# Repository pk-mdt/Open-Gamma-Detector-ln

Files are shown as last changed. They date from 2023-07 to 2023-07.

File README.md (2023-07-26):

# Open Gamma Detector

**This is a revised hardware design from the original 3.0 version of the project. The project has been redesigned in Kicad and incorporates an impedance controlled 4 layer board design, as well as micro SMA connectors to the SiPM**

These changed from the original project are hardware only, the original software works and has been fully tested on these revisions. Here is an assembled prototype with a Sodium Iodide Crystal from OST Photonics.

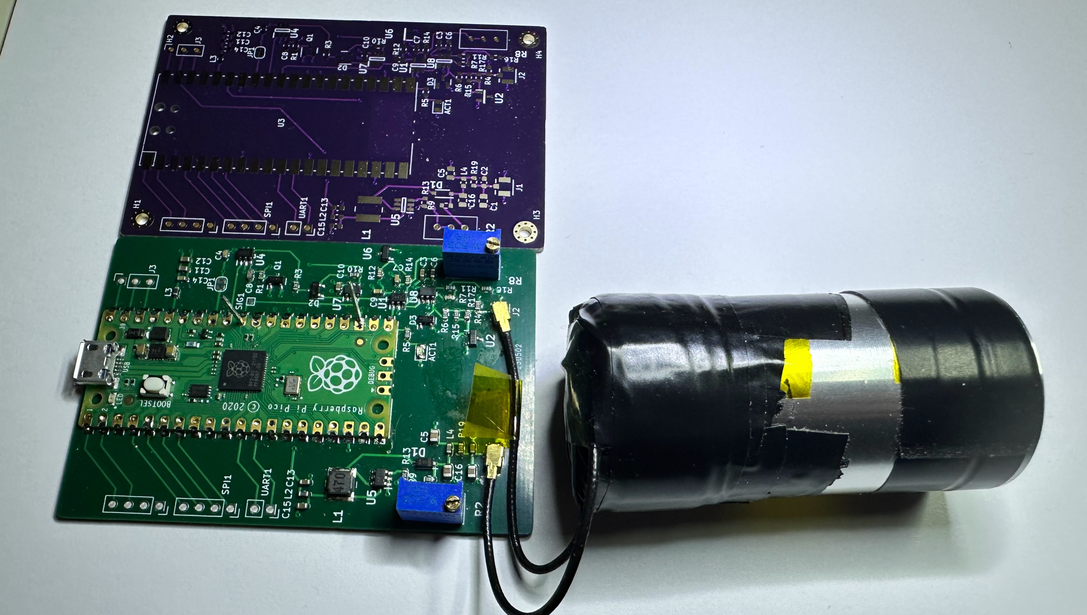
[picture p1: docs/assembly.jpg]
Assembled Detector and Latest Bare Board


Revised custom layout and hardware for a hackable scintillation counter and multichannel analyzer (MCA) all-in-one device using a popular NaI(Tl) scintillation crystal and a silicon photomultiplier (SiPM). Extremely affordable design for a DIY gamma spectroscopy setup with a total parts cost of under around 200 USD.

The detector uses a standard serial-over-USB connection so that it can be integrated into as many other projects as possible, for example data logging with a Raspberry Pi, weather stations, Arduino projects, etc.

If you want a barebone version of the Open Gamma Detector to count pulses or something like that, you can have a look at the [Mini SiPM Driver](https://github.com/OpenGammaProject/Mini-SiD) board.

## Features

Here are some of the most important specs:

* Compact design: Total size 77 x 50 mm.
* All-in-one: No external parts (e.g. sound card) required to record gamma spectra.
* Easily programmable using drag-and-drop firmware files or the standard Arduino IDE.
* Low-voltage device: No HV needed like with photomultiplier tubes.
* Can use SiPMs in the voltage range of 27.5 V to 33.8 V.
* 4096 ADC channels with built-in 3 V voltage reference.
* Revised Energy resolution of ~6% @ 662 keV possible; highly dependent on your SiPM/scintillator assembly.
* Default (Energy) Mode: About 15 µs total dead time while measuring energy.
* Geiger Mode: About 5 µs total dead time without energy measurements.
* Low power consumption: ~25 mA @ 5 V with default firmware.
* Additional broken-out power pins and I2C, SPI and UART headers for custom parts (e.g. display, µSD card, etc.).
* Built-in True Random Number Generator.
* Simple OLED support out of the box (SSD1306 and SH110x).
* Built-in customizable ticker support.

## Working Principle

Here is a nice flow chart to describe how the device roughly works:

Working Principle Flow Chart

## Hardware

Hardware design has been done with Kicad and all the needed files for you to import the project as well as the schematic can be found in the `hardware` folder. There is also a Gerber file available for you to go directly to the PCB manufacturing step.

Detailed information about the hardware of the detector as well as the potentiometer settings and assembly can be found in the [hardware directory](/hardware/).

## Software

The software aims to be as simple as possible to understand and maintain. To achieve this I decided to use an off-the-shelf microcontroller - the [Raspberry Pi Pico](https://www.raspberrypi.com/products/raspberry-pi-pico/). This board can be programmed with the Arduino IDE over micro-USB and is powerful (dual core, fast ADC, plenty of memory, ...) enough for the purpose and also exceptionally cheap.

To program the Pico and/or play around with the firmware, head to the [software directory](/software/). There you will also find documentation on the serial interface (!), display support, and much more.

## Example Spectra

Coming Soon

## Known Limitations

1. The Raspberry Pi Pico's ADC has some pretty [severe DNL issues](https://pico-adc.markomo.me/INL-DNL/#dnl) that result in four channels being much more sensitive (wider input range) than the rest. For now the simplest solution was to discard all four of them, by printing a `0` when any of them comes up in the measurement (to not affect the cps readings). You can turn this behavior off by using the `set correction` command. This is by no means perfect or ideal, but it works for now until this gets fixed in a later hardware revision of the RP2040 (wish us luck!).

2. Due to the global parts shortage many chips are much harder to come by, if at all that is. Parts that are listed in the BOM should be available easily and with high reliability and stock so that they don't run out quickly. Please let me know if you cannot find a part anymore.

3. The power supply is currently **not** temperature corrected, meaning changes in the ambient temperature with a constant voltage affect the gain of the SiPM. This will naturally result in a different DC bias, energy range and S/N ratio. This effect is negligible around room temperature, though. The temperature dependence of the gain is -0.8%/°C (21°C) for the MicroFC SiPMs.

## Troubleshooting and FAQ

Please have a look at [REFERENCE.md](REFERENCE.md) for some general guidance.

If this doesn't help you, feel free to reach out and create an issue or open a discussions thread.

## Some Ideas

### Coincidence Measurements

Using multiple detector boards with some firmware modifications it should be theoretically possible to implement a coincidence measurement feature. By respectively connecting the `VSYS`, `GND` and one of the broken-out pins to each other on both boards you have everything you need to get started. The pins would be used for an interrupt from the child detector to the parent to trigger a pulse if both timings coincide.

At the moment, though, I couldn't get a coincidence mode feature running due to some weird timing issues. There might be a firmware update in the future to implement this feature. If you have any ideas, let me know!

### Cooling the SiPM

During operation all the electronics including the SiPM naturally heat up ever so slightly. Due to the detector board (where most of the power is dissipated) not being directly connected to the SiPM self-heating is negligible, though. Therefore air or water cooling alone won't improve performance considerably, because it won't heat up much above ambient temps, if at all that is. However, you could cool the SiPM PCB with a Peltier module to sub-ambient temperatures. According to the [datasheet AND9770 (Figure 27)](https://www.onsemi.com/pub/Collateral/AND9770-D.PDF) every 10°C reduction in temperature decreases the dark count rate by 50%! But be sure to correct the SiPM voltage (overvoltage) in this case as it also changes with temperature.

Note that the required breakdown voltage of the SiPM increases linearly with 21.5 mV/°C, see the [C-Series SiPM Sensors Datasheet](https://www.onsemi.com/pdf/datasheet/microc-series-d.pdf). This means that you would also need to temperature correct the PSU voltage if you wanted to use it with considerably different temperatures.

### Shielding Background Radiation

Shielding the ambient background can be done ideally using a wide enough layer of lead (bricks) all around the detector with a thin layer of lower-Z material on the inside such as copper to avoid backscattering. The SiPM and the sample can then be put into the structure to get the best measurements possible (low background).

See Wikipedia: [Lead Castle](https://en.wikipedia.org/w/index.php?title=Lead_castle&oldid=991799816)

---

Thanks for reading.

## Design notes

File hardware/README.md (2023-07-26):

# Hardware

_Here you can find everything you need to build yourself a detector, or more._

This project utilizes a silicon photomultiplier (short SiPM) which is way smaller and more robust than a traditional photomultiplier tube and does not need a high-voltage supply (traditionally ~1000 V).

The following 6 mm SiPMs are recommended for this project:

* **MICROFC-60035-SMT-TR**
* MICROFC-60035-SMT-TR1 (the exact same as above, however will be more expensive to purchase as sold in smaller batches to suppliers)
* AFBR-S4N66C013 (a good replacement if the above are unavailable)

Here are some very helpful in-depth datasheets about the particular MicroFC SiPM recommended here:

* [C-Series SiPM Sensors datasheet](https://www.onsemi.com/pdf/datasheet/microc-series-d.pdf)
* [Linearity of the Silicon Photomultiplier](https://www.onsemi.com/pub/Collateral/AND9776-D.PDF)
* [Introduction to the SiliconPhotomultiplier (SiPM)](https://www.onsemi.com/pub/Collateral/AND9770-D.PDF)
* [Biasing and Readout of ON Semiconductor SiPM Sensors](https://www.onsemi.com/pub/Collateral/AND9782-D.PDF)

The hardware consists of the main detector (hardware in this folder) which includes amplification, pulse detection and energy measurement. If you already have a SiPM/crystal assembly compatible with voltages around 30 V, you may use it with the detector board and connecting wires directly to the correct pads. Otherwise, you can use my [SiPM carrier board](https://github.com/OpenGammaProject/MicroFC-SiPM-Carrier-Board), which holds the SiPM and all the optional decoupling. There is also a carrier board for the Broadcom SiPM.

The heart of the detector board is the Raspberry Pi Pico which uses its ADC to measure the pulse amplitude (i.e. the energy) immediately after an event occurs starting with an interrupt. I can really recommend you reading the datasheet or maybe also having a look at a deeper analysis of the Pico ADC, if you're interested:

* [Raspberry Pi Pico](https://datasheets.raspberrypi.com/pico/pico-datasheet.pdf)
* [Characterizing the Raspberry Pi Pico ADC](https://pico-adc.markomo.me/)

Here is sa front render of the detector PCB. Size is about 77 x 50 mm. 

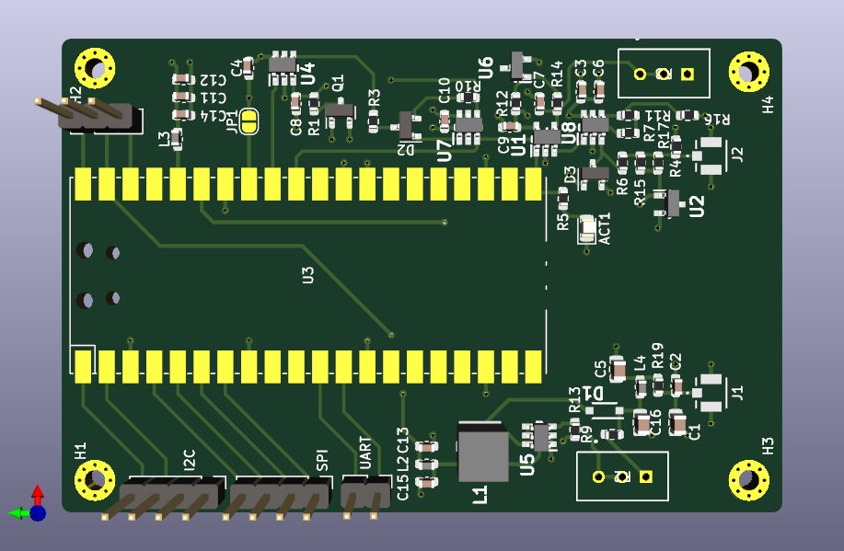
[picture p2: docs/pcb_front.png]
Front Side PCB


On the front side of the PCB at JP1 there is also a jumper to connect the analog ground to the rest of the ground plane. You can solder that if you want to, if you know exactly what you're doing. It's not needed, though.

There are also broken-out pins for the power supply, I2C, SPI and UART connections. These can be used to modify the device, e.g. by adding a display or using a battery charger. You can have a look at the great [Raspberry Pi Pico datasheet](https://datasheets.raspberrypi.com/pico/pico-datasheet.pdf) for more info on this.

Some more info on the peripheral headers can be found in the `software` section of this project.

## Pinout

Header Pinout

You can also put a little jumper from `VBUS` to `VSYS` if you **only** want to use the detector with the USB connection on the Pico. This bridges a diode on the Raspberry Pi Pico and saves you a couple of mW.

## Potentiometers

Here is a helpful image about the potentiometer settings for revision 3.0, it's not complicated:

Potentiometer Controls

As you can see it is pretty easy to set the required voltage and threshold. **As a general rule, turn any potentiometer clockwise to increase the parameters, turn anti-clockwise to decrease.**

## Scintillator (Assembly)

The finished [MicroFC-](https://github.com/OpenGammaProject/MicroFC-SiPM-Carrier-Board) and [AFBR-](https://github.com/OpenGammaProject/AFBR-SiPM-Carrier-Board) SiPM carrier boards are there to allow for easier packaging with the scintillator as well as to be reusable for different detectors as that's by far the single most expensive part and you'll want to use it as long as possible.

If you are using a larger-diameter scintillator, it might be better for you to use something like the [MicroFC SiPM Array Board](https://github.com/OpenGammaProject/MicroFC-SiPM-Array-Board), which has a 2x2 matrix of SiPMs resulting in 4x the active area. This can increase the energy resolution for large crystals.

### Scintillator Cyrstals

I got all of my scintillators (used NaI(Tl), LYSO, ...) on eBay. Just search for some keywords or specific types, you'll probably find something. Just be sure to look out for signs of wear and tear like scratches on the window or yellowing (!) in NaI crystals as these can deteriorate performance significantly.

You can obviously also buy brand-new scintillators, however, these can be much more expensive. It really depends on the manufacturer there. You can get some cheap 1" x 1" NaI(Tl) scintillator from China for < $100.

Two sources of new NaI(Tl) scintillators are:

| Brand | Location | Comment |
|-------|----------|---------|
|[OST - Photonics](https://www.ost-photonics.com/products/scintillation-crystal/encapsulated-scintillator/standard-type-naitl-scintillator/)| China | Can purchase directly from website |
| [Epic-Crystal](https://www.epic-crystal.com/) | China | Also sold by [GammaSpectacular](https://www.gammaspectacular.com/)

**Since this is a fixed-gain device, I can only highly recommend you to get a scintillator that fits on the PCB and is of a comparable volume as the scintillators I tested. I am using an 18 x 30 mm crystal for most of the spectra that you can see here and it works great. Also, due to the small size of the SiPM in comparison to the scintillator opening, try to use narrower crystals than wider ones if you can.** That way, there aren't many light losses to the SiPM. In general, just be sure the volume/size is not orders of magnitue larger or smaller. If that's not possible, consider using the array board.

If the scintillator is too small, the output voltage too will be very low and you might get restricted by the ADC resolution. In this case the energy range will also be much higher than you would ever need (can easily get up to 10 MeV).

If the scintillator is too large, the output voltages will be very high and thus decrease your energy range dramatically. The device is limited by the 3.0 V reference voltage in this case!

**As a general rule of thumb, try to use as much of the space available on the PCB as possible to mount the scintillator and you will (in most cases) be absolutely fine.**

### Index-Matching Material

You should apply some optical coupling compound between the SiPM and the crystal window to reduce reflections as good as possible (this way the best photon detection efficiency is achieved). There a multitude of options for optical couplants, and depending on your region some may be easier to aquire than others. As a general rule of thumb, silicone oil/grease can be used. If it contains polydimethylsiloxane, you're on the right track. Some options:

<!---This is a good source https://www.logwell.com/tech/servtips/optical_coupling_grease.html - Sebyon --->

| Description            | Brand  | Reflective Index | Viscosity (cPs)| Cost (USD) | Comment |
|------------------------|--------|------------------|----------------|------------|---------|
|[Index Matching Gel, 3 cc](https://www.thorlabs.com/thorproduct.cfm?partnumber=G608N3)|Thorlabs| 1.43 | 1,060,000 | $47.46 | High viscosity, works well for fibre optic coupling. |
|[Index-Matching Fluid](https://www.newport.com/f/index-matching-fluid) | Newport | 1.52 | 100 | $45.60 | Low viscosity may make setting the SiPM and crystal window difficult. However, the RI is the closer to the window properties. Use if you're experienced with assembly. |
|XIAMETER™ PMX-200 Silicone Fluid | Dow Corning | 1.40 | 60,000 - 100,000 | Depends on source | Low cost and [used in research](https://pubs.acs.org/doi/10.1021/acs.cgd.0c00256) due to performance / price. PMX-200 can come in various viscosities, try to get close to 100,000 cPs. |
|Molykote Industrial 4 Electrical Insulating Compound | Dow Corning | N/A | Grease | ~$20 | Used by Ludlum for their survey meter scintillation detectors. |

<!--- I might add some more options for achieving a hermatic seal with tape here once I start putting one together - Sebyon --->

After you applied some, you press both parts together and wrap everything with light-tight tape, again, I'm just using some black electrical tape here. That's essentially it, now you can solder some wires to the pads on the board to connect them together and secure it in place in the free space on the board.

It's very important to get the SiPM/scintillator assembly light-tight. Otherwise you'll either run into problems with lower energies where noise dominates or outright not measure anything at all, because the sensor is saturating.

**==> More assembly instructions can be found on the [Hackaday.io project page](https://hackaday.io/project/185211/instructions)!**

## Raspberry Pi Pico W

Since the Pico W has functionally the exact same size and pinout, it can be a trivial replacement for the standard Pico. This can be a great place to start experimenting with connecting to the Open Gamma Detector via Bluetooth or WiFi, there are endless possibilities what you can do with that.

If you switch to the Pico W, though, you will need to modify the stock firmware slightly since internal pins like the input voltage pin are changed.

There is also no firmware build for the Pico W and I don't plan to make one in the near future, since I'm busy enough with the stock firmware, hardware and Gamma MCA, to start building yet another Bluetooth- or WiFi-connected app or whatever.

I'll happily accept PRs if you make something like that, though, so let me know! ;)

## Shielding

Due to the detector measuring small voltages, energy resolution being limited by noise and a small 470 pF capacitor being on board, it is generally pretty sensitive to EMI. For the best performance possible, you should put your detector into some kind of metal enclosure. It doesn't need to be a thick metal case, a tin can will most likely suffice.

<!--- Once I start assembly I'll look at proving some shielding ideas - Sebyon --->

The four screw holes on the PCB's actual detector part are connected to the circuit GND.

As some level of protection against EMI, the peak and hold capacitor is periodically discharged as to avoid it being charged ever so slightly by interference. This takes place every millisecond by default and cannot be switched on or off via a serial command. This adds less than 1% of additional dead time (~2.5 µs per reset), so should be completely negligible.

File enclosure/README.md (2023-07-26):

**Note, this fork has significant changes to the PCB size, once I get the enclosure designed for it the relevant 3D files will be uploaded here.**

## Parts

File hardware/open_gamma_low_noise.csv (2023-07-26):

Source: | C:\Users\kileypat\Documents\open_gamma_nano\open_gamma_low_noise\open_gamma_low_noise_v2\open_gamma_low_noise_v2.kicad_sch
Date: | 7/25/2023 6:13:00 PM
Tool: | Eeschema 7.0.2-27-g7a50654f3b
Generator: | C:\Program Files\KiCad\7.0\bin\scripting\plugins/bom_csv_grouped_by_value.py
Component Count: | 62
Collated Components:
Item | Qty | Reference(s) | Value | LibPart | Footprint | Datasheet | DNP | Height | Manufacturer_Name | Manufacturer_Part_Number | Mouser Part Number | Mouser Price/Stock
1 | 1 | ACT1 | LED | Device:LED | LED_SMD:LED_0805_2012Metric | ~ |  |  | broadcom | HSML-C170 | 630-HSML-C170
2 | 3 | C1, C5, C16 | 4.7uF | Device:C | Capacitor_SMD:C_0805_2012Metric | ~ |  |  | Samsung | CL21A475KBQNNNE | 187-CL21A475KBQNNNE
3 | 6 | C2, C3, C4, C7, C9, C14 | 100nf | Device:C | Capacitor_SMD:C_0603_1608Metric | ~ |  |  | TDK | C0603X5R1E104K030BB | 810-C0603X5R1E104KBB
4 | 6 | C6, C10, C11, C12, C13, C15 | 10uf | Device:C | Capacitor_SMD:C_0603_1608Metric | ~ |  |  | Kyocera | 06036D106MAT2A | 581-06036D106MAT2A
5 | 1 | C8 | 470pf | Device:C | Capacitor_SMD:C_0603_1608Metric | ~ |  |  | Panasonic | ECH-U1C471JX5 | 667-ECH-U1C471JX5
6 | 1 | D1 | PMEG4010CEGWJ | Device:D_Schottky | LIB_PMEG6010CEH,115:SODFL3516X120N | ~ |  |  | Nexperia | PMEG6010CEH,115 | 771-PMEG6010CEH-T/R
7 | 2 | D2, D3 | BAT54S | Diode:BAT54S | Package_TO_SOT_SMD:SOT-23 | https://www.diodes.com/assets/Datasheets/ds11005.pdf |  |  | Nexperia | BAT54S,215 | 771-BAT54S-T/R
8 | 4 | H1, H2, H3, H4 | ~ | Mechanical:MountingHole_Pad | MountingHole:MountingHole_2.2mm_M2_Pad_Via | ~
9 | 1 | I2C1 | ~ | Connector:Conn_01x04_Pin | Connector_PinSocket_2.54mm:PinSocket_1x04_P2.54mm_Vertical | ~
10 | 2 | J1, J2 | 1909763-1 | SMD_Coax:1909763-1 | SMD_Coax:CONN3_1909763_TEC | 1909763-1 |  |  | TE Connectivit/AMP | 1909763-1 | 571-1909763-1
11 | 1 | J3 | ~ | Connector:Conn_01x03_Pin | Connector_PinSocket_2.54mm:PinSocket_1x03_P2.54mm_Vertical | ~
12 | 1 | JP1 | Jumper_2_Open | Jumper:Jumper_2_Open | Jumper:SolderJumper-2_P1.3mm_Open_RoundedPad1.0x1.5mm | ~
13 | 1 | L1 | 47 uH | Device:L | SamacSys_Parts2:74404054470 | ~ |  |  | Wurth | 74404054470 | 710-74404054470
14 | 1 | L2 | 1k Ohm | Device:L | Inductor_SMD:L_0603_1608Metric | ~ |  |  |  | BLM18KG102SN1D | 81-BLM18KG102SN1D
15 | 1 | L3 | 1k Ohm | Device:L | Inductor_SMD:L_0603_1608Metric | ~ |  |  |  | BLM18KG102SN1D | 81-BLM18KG102SN1D
16 | 1 | L4 | 1 k Ohm | Device:L | Inductor_SMD:L_0603_1608Metric | ~ |  |  |  | BLM18KG102SN1D | 81-BLM18KG102SN1D
17 | 1 | Q1 | 2N7002,215 | Transistor_FET:2N7002 | Package_TO_SOT_SMD:SOT-23 |  |  |  |  | 2N7002,215 | 771-2N7002-T/R
18 | 7 | R1, R4, R5, R7, R11, R12, R16 | 1k | Device:R | Resistor_SMD:R_0603_1608Metric | ~ |  |  |  | 0603WAF1001T5E | 303-0603WAF1001T5E
19 | 2 | R2, R8 | 50k | Device:R_Potentiometer_US | 3296W-1-103:3296W1103 | ~ |  |  |  | 3296W-1-503LF | 652-3296W-1-503LF
20 | 2 | R3, R13 | 10k | Device:R | Resistor_SMD:R_0603_1608Metric | ~ |  |  |  | 0603WAF1002T5E | 303-0603WAF1002T5E
21 | 3 | R6, R10, R19 | 100 | Device:R | Resistor_SMD:R_0603_1608Metric | ~ |  |  |  | 0603WAF1000T5E | 303-0603WAF1000T5E
22 | 4 | R9, R14, R15, R17 | 210k | Device:R | Resistor_SMD:R_0603_1608Metric | ~ |  |  |  | 0603WAF2103T5E | 303-0603WAF2103T5E
23 | 1 | SPI1 | Conn_01x04_Pin | Connector:Conn_01x04_Pin | Connector_PinSocket_2.54mm:PinSocket_1x04_P2.54mm_Vertical | ~
24 | 1 | U1 | TLV3201AIDBVR | SamacSys_Parts:TLV3201AIDBVR | SamacSys_Parts2:SOT95P280X145-5N | http://www.ti.com/lit/gpn/tlv3201 |  | 1.45 | Texas Instruments | TLV3201AIDBVR | 595-TLV3201AIDBVR | https://www.mouser.co.uk/ProductDetail/Texas-Instruments/TLV3201AIDBVR?qs=5771e39Rz9GGuYwPEKy7fA%3D%3D
25 | 2 | U2, U6 | LM4040AIM3-3.0+T | SamacSys_Parts:LM4040AIM3-3.0+T | SamacSys_Parts2:SOT95P237X112-3N | https://pdfserv.maximintegrated.com/en/ds/LM4040.pdf |  | 1.12 | Analog Devices | LM4040AIM3-3.0+T | 700-LM4040AIM3-3.0T | https://www.mouser.co.uk/ProductDetail/Maxim-Integrated/LM4040AIM3-3.0%2bT?qs=GxOUx7aO6nwPVxQkEMnXjg%3D%3D
26 | 1 | U3 | Pico | MCU_RaspberryPi_and_Boards:Pico | MCU_RaspberryPi_and_Boards:RPi_Pico_SMD_TH |  |  |  |  | SC0915 | 358-SC0915
27 | 3 | U4, U7, U8 | OPA357AIDBVTG4 | SamacSys_Parts:OPA357AIDBVTG4 | SamacSys_Parts2:SOT95P280X145-6N | https://www.ti.com/lit/ds/symlink/opa357.pdf?ts=1640505454363 |  | 1.45 | Texas Instruments | OPA357AIDBVTG4 | 595-OPA357AIDBVTG4 | https://www.mouser.co.uk/ProductDetail/Texas-Instruments/OPA357AIDBVTG4?qs=SnxTrzcm0GjRMGlI%252BeOozg%3D%3D
28 | 1 | U5 | MAX5026EUT+T | SamacSys_Parts:MAX5026EUT+T | SamacSys_Parts2:SOT95P280X145-6N | https://datasheets.maximintegrated.com/en/ds/MAX5025-MAX5028.pdf |  | 1.45 | Analog Devices | MAX5026EUT+T | 700-MAX5026EUTT | https://www.mouser.co.uk/ProductDetail/Maxim-Integrated/MAX5026EUT%2bT?qs=Mqkh4jHMT8zfiFUMsw6rrA%3D%3D
29 | 1 | UART1 | Conn_01x02 | Connector_Generic:Conn_01x02 | Connector_PinSocket_2.54mm:PinSocket_1x02_P2.54mm_Vertical | ~

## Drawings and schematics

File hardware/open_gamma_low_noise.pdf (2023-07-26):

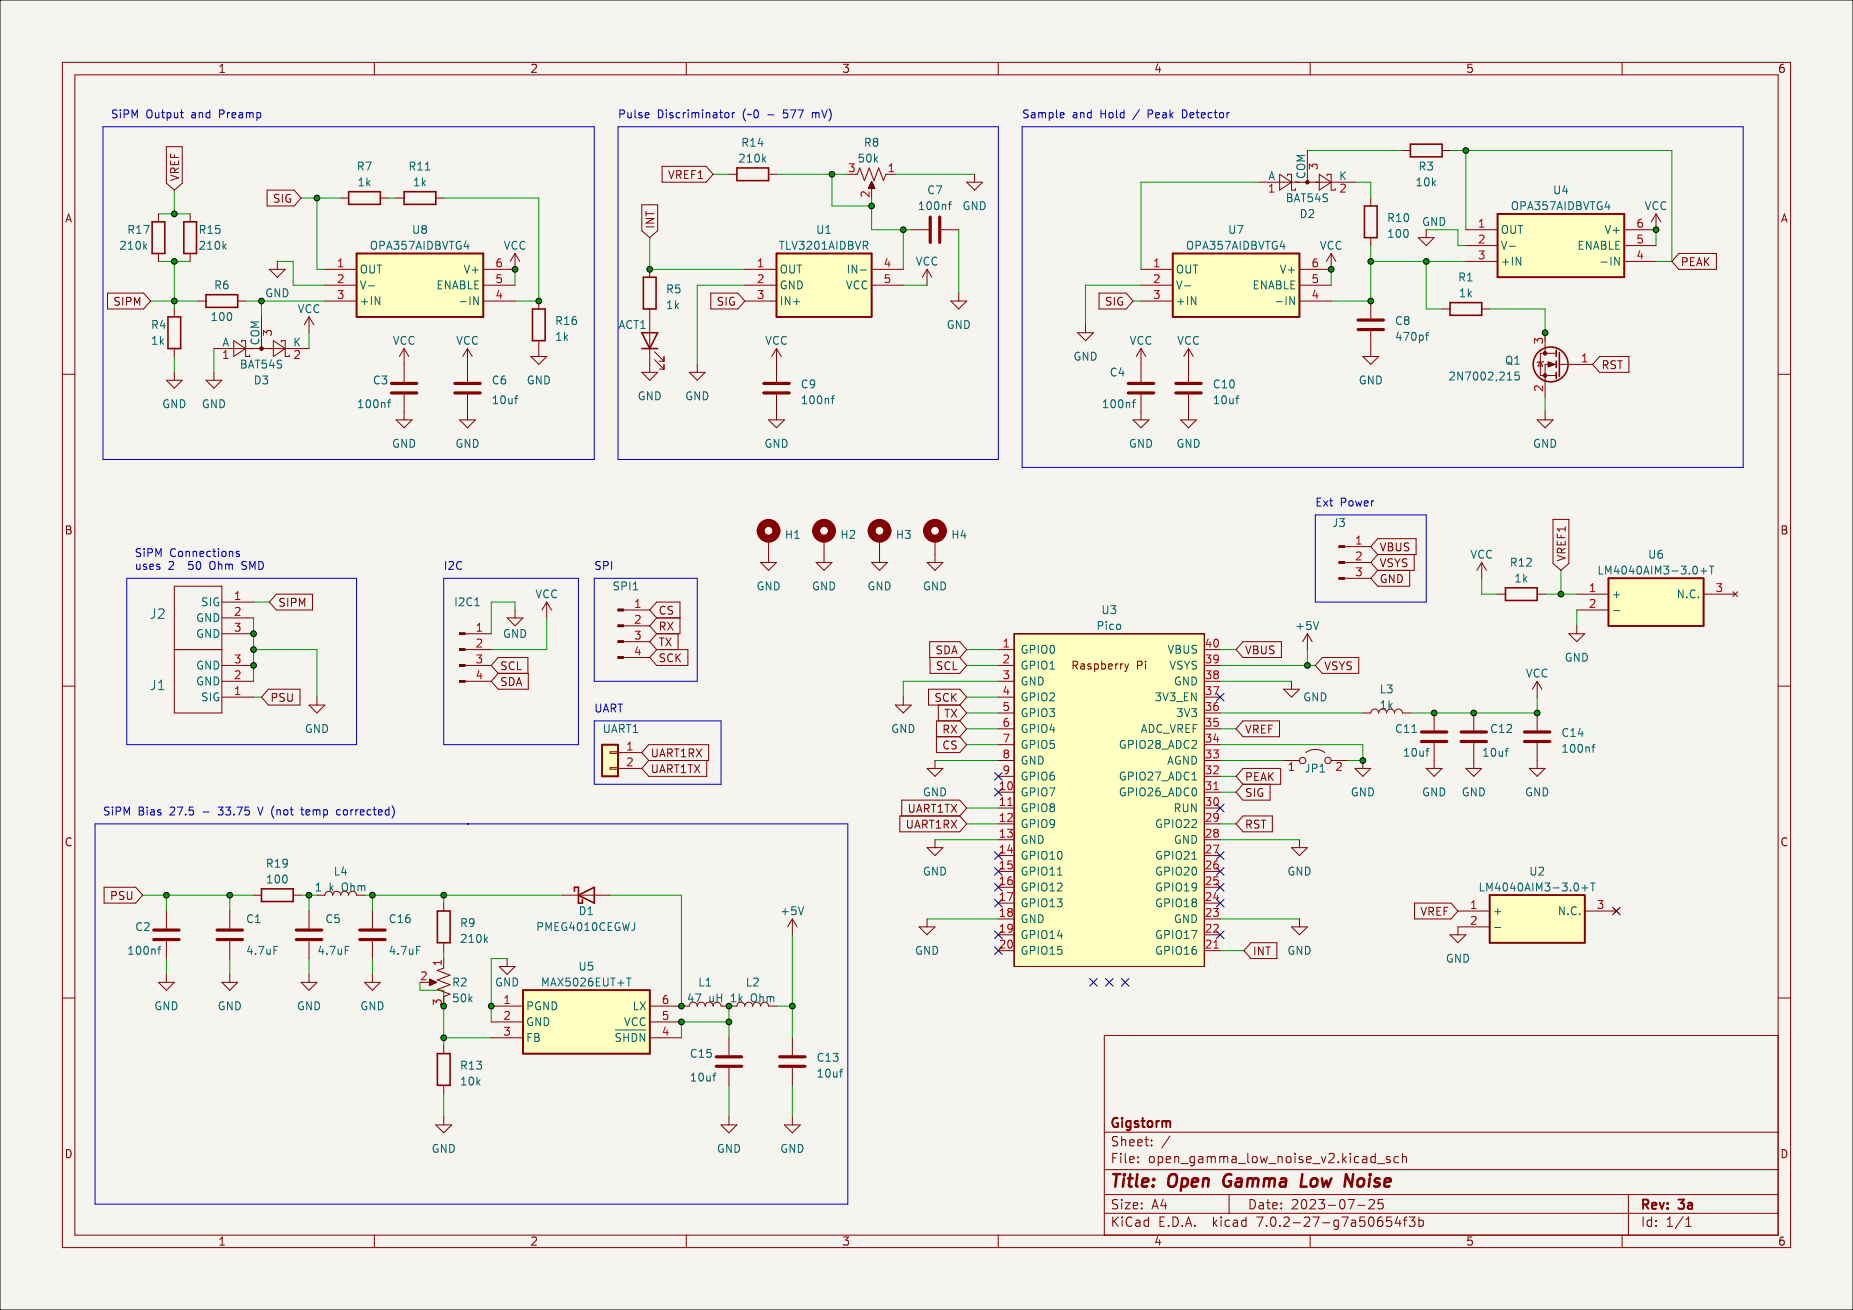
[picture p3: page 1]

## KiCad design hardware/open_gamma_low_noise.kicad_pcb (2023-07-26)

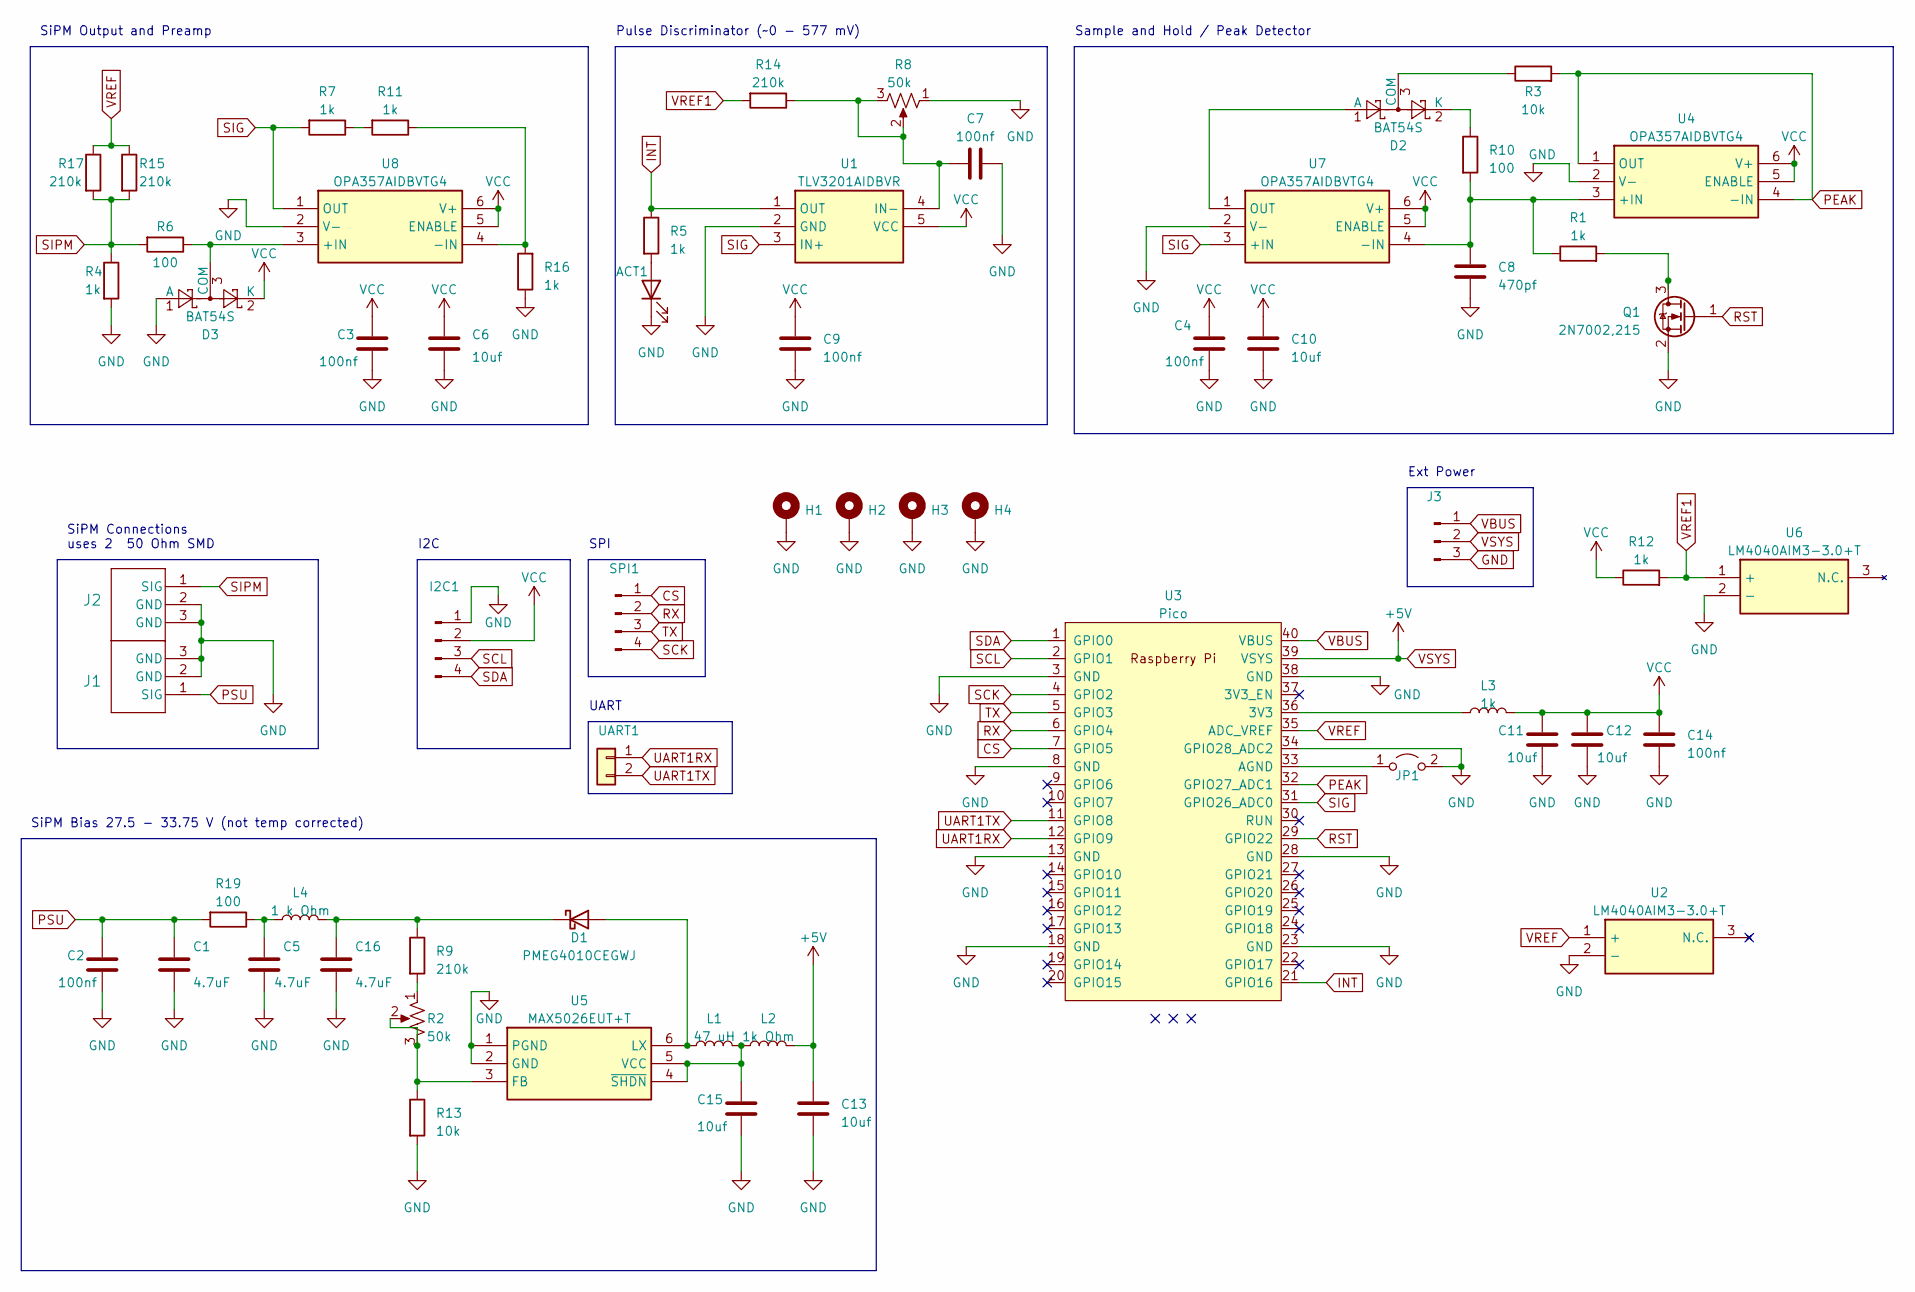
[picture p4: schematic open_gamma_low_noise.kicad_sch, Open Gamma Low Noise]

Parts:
ACT1: LED; LED_0805_2012Metric
C1, C5, C16: 4.7uF; C_0805_2012Metric
C2, C3, C4, C7, C9, C14: 100nf; C_0603_1608Metric
C6, C10, C11, C12, C13, C15: 10uf; C_0603_1608Metric
C8: 470pf; C_0603_1608Metric
D1: PMEG4010CEGWJ; SODFL3516X120N
D2, D3: BAT54S; SOT-23
H1, H2, H3, H4: MountingHole_2.2mm_M2_Pad_Via
I2C1: PinHeader_1x04_P2.54mm_Vertical
J1, J2: 1909763-1; CONN3_1909763_TEC
J3: PinHeader_1x03_P2.54mm_Vertical
JP1: Jumper_2_Open; SolderJumper-2_P1.3mm_Open_RoundedPad1.0x1.5mm
L1: 47 uH; 74404054470
L2: 1k Ohm; L_0603_1608Metric
L3: 1k; L_0603_1608Metric
L4: 1 k Ohm; L_0603_1608Metric
Q1: 2N7002,215; SOT-23
R1, R4, R5, R7, R11, R12, R16: 1k; R_0603_1608Metric
R2, R8: 50k; POT_3296W
R3, R13: 10k; R_0603_1608Metric
R6, R10, R19: 100; R_0603_1608Metric
R9, R14, R15, R17: 210k; R_0603_1608Metric
SPI1: Conn_01x04_Pin; PinHeader_1x04_P2.54mm_Vertical
U1: TLV3201AIDBVR; SOT95P280X145-5N; Mouser Part Number 595-TLV3201AIDBVR
U2, U6: LM4040AIM3-3.0+T; SOT95P237X112-3N; Mouser Part Number 700-LM4040AIM3-3.0T
U3: Pico; RPi_Pico_SMD_TH
U4, U7, U8: OPA357AIDBVTG4; SOT95P280X145-6N; Mouser Part Number 595-OPA357AIDBVTG4
U5: MAX5026EUT+T; SOT95P280X145-6N; Mouser Part Number 700-MAX5026EUTT
UART1: Conn_01x02; PinHeader_1x02_P2.54mm_Vertical

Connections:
CS: SPI1.1, U3.7 (GPIO5); also elsewhere on the board
GND: ACT1.1 (K), C1.2, C2.2, C3.2, C4.2, C5.2, C6.2, C7.2, C8.2, C9.2, C10.2, C11.2, C12.2, C13.2, C14.2, C15.2, C16.2, D3.1 (A), H1.1, H2.1, H3.1, H4.1, I2C1.1, J1.2 (GND), J1.3 (GND), J2.2 (GND), J2.3 (GND), J3.3, JP1.2 (B), Q1.2 (S), R4.2, R8.1, R13.2, R16.1, U1.2 (GND), U2.2 (-), U3.3 (GND), U3.8 (GND), U3.13 (GND), U3.18 (GND), U3.23 (GND), U3.28 (GND), U3.34 (GPIO28_ADC2), U3.38 (GND), U4.2 (V-), U5.1 (PGND), U5.2 (GND), U6.2 (-), U7.2 (V-), U8.2 (V-); also elsewhere on the board
INT: R5.1, U1.1 (OUT), U3.21 (GPIO16)
unnamed: ACT1.2 (A), R5.2
unnamed: C5.1, L4.1, R19.1
unnamed: D1.2 (A), L1.1, U5.6 (LX)
unnamed: C16.1, D1.1 (K), L4.2, R9.1
unnamed: D2.1 (A), U7.1 (OUT)
unnamed: D2.3 (COM), R3.1
unnamed: D2.2 (K), R10.1
unnamed: D3.3 (COM), R6.1, U8.3 (+IN)
unnamed: JP1.1 (A), U3.33 (AGND)
unnamed: Q1.3 (D), R1.2
unnamed: R2.1, R9.2
unnamed: R7.1, R11.2
unnamed: C7.1, R8.2, R8.3, R14.1, U1.4 (IN-)
unnamed: L3.1, U3.36 (3V3)
unnamed: C8.1, R1.1, R10.2, U4.3 (+IN), U7.4 (-IN)
unnamed: R2.2, R2.3, R13.1, U5.3 (FB)
unnamed: C15.1, L1.2, L2.1, U5.4 (~SHDN), U5.5 (VCC)
unnamed: R11.1, R16.2, U8.4 (-IN)
PEAK: R3.2, U3.32 (GPIO27_ADC1), U4.1 (OUT), U4.4 (-IN)
PSU: C1.1, C2.1, J1.1 (SIG), R19.2
RST: Q1.1 (G), U3.29 (GPIO22)
RX: SPI1.2, U3.6 (GPIO4); also elsewhere on the board
SCK: SPI1.4, U3.4 (GPIO2); also elsewhere on the board
SCL: I2C1.3, U3.2 (GPIO1); also elsewhere on the board
SDA: I2C1.4, U3.1 (GPIO0); also elsewhere on the board
SIG: R7.2, U1.3 (IN+), U3.31 (GPIO26_ADC0), U7.3 (+IN), U8.1 (OUT)
SIPM: J2.1 (SIG), R4.1, R6.2, R15.2, R17.2
TX: SPI1.3, U3.5 (GPIO3); also elsewhere on the board
UART1RX: U3.12 (GPIO9), UART1.1; also elsewhere on the board
UART1TX: U3.11 (GPIO8), UART1.2; also elsewhere on the board
VBUS: J3.1, U3.40 (VBUS)
VCC: C3.1, C4.1, C6.1, C9.1, C10.1, C11.1, C12.1, C14.1, D3.2 (K), I2C1.2, L3.2, R12.1, U1.5 (VCC), U4.5 (ENABLE), U4.6 (V+), U7.5 (ENABLE), U7.6 (V+), U8.5 (ENABLE), U8.6 (V+); also elsewhere on the board
VREF: R15.1, R17.1, U2.1 (+), U3.35 (ADC_VREF)
VREF1: R12.2, R14.2, U6.1 (+)
VSYS: C13.1, J3.2, L2.2, U3.39 (VSYS)

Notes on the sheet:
SPI
Ext Power
Pulse Discriminator (~0 - 577 mV)
SiPM Output and Preamp
I2C
Sample and Hold / Peak Detector
SiPM Bias 27.5 - 33.75 V (not temp corrected)
UART
SiPM Connections uses 2 50 Ohm SMD

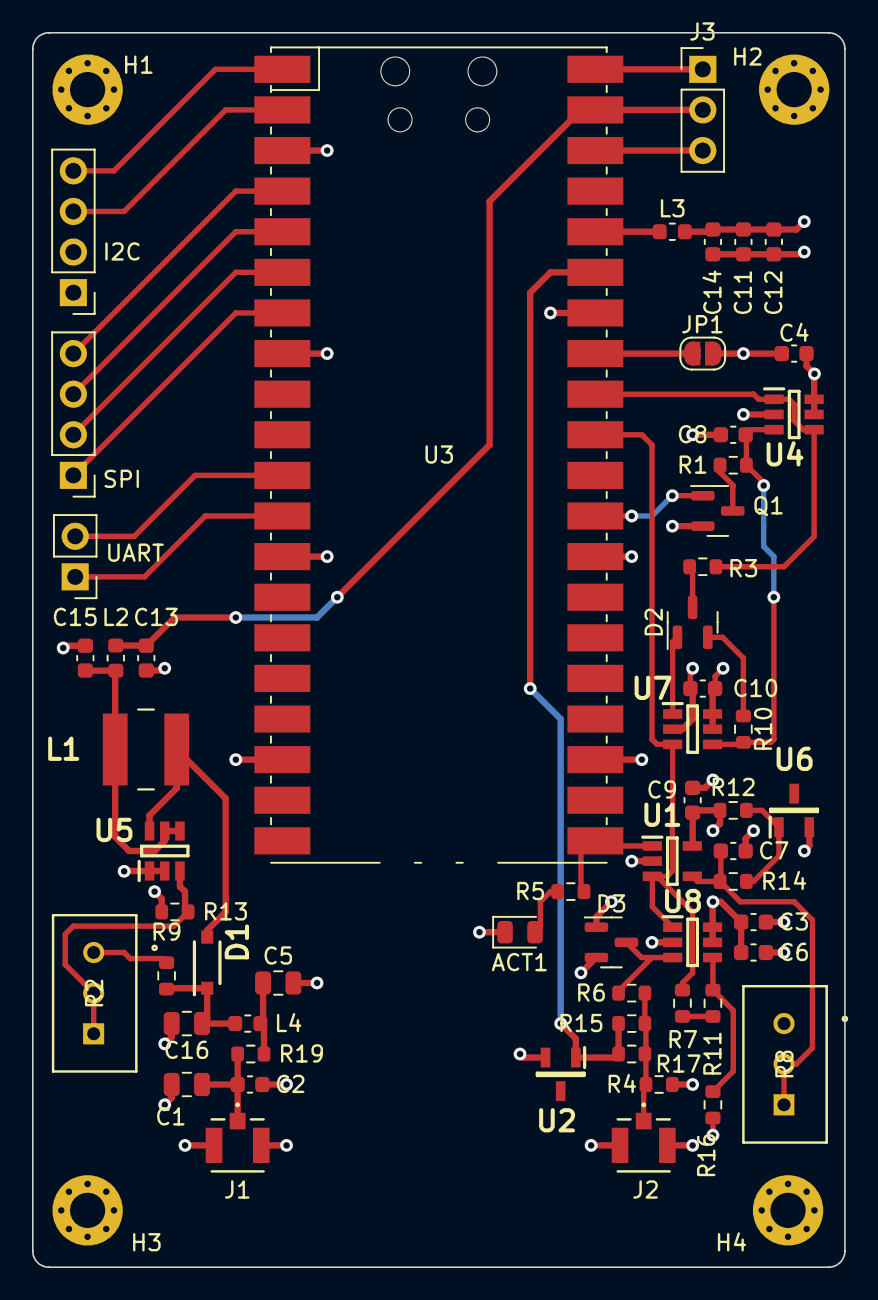
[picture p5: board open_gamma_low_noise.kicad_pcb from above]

Board: 4 copper layers, 50.8 x 77.2 mm, 62 parts (0 on the bottom side), 38 nets.

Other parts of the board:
I2C: PinHeader_1x04_P2.54mm_Vertical
SPI: Conn_01x04_Pin; PinHeader_1x04_P2.54mm_Vertical
UART: Conn_01x02; PinHeader_1x02_P2.54mm_Vertical

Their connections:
CS: SPI.1; also elsewhere on the board
GND: I2C.1; also elsewhere on the board
RX: SPI.2; also elsewhere on the board
SCK: SPI.4; also elsewhere on the board
SCL: I2C.3; also elsewhere on the board
SDA: I2C.4; also elsewhere on the board
TX: SPI.3; also elsewhere on the board
UART1RX: UART.1; also elsewhere on the board
UART1TX: UART.2; also elsewhere on the board
VCC: I2C.2; also elsewhere on the board

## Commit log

2023-07-26 Low Noise Hardware Revisions
    Changed to 4 layer impedance controlled board. Redesigned using kicad.
    [BOM.csv, Drill_NPTH_Through.DRL, Drill_PTH_Through.DRL, Drill_PTH_Through_Via.DRL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]
2023-07-26 Removed Enclosure
    Removed 3D files until rework completed
    [Case_Body_ReducedHeight_USB-B.STL, Case_Body_ReducedHeight_micro-USB.STL, Case_Body_USB-B.STL, Case_Body_micro-USB.STL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]
2023-07-26 Update README.md
    Remove Case References (for now)
2023-07-26 Updated 3D models
    [open_gamma_low_noise.kicad_pcb, open_gamma_low_noise.kicad_sch]
